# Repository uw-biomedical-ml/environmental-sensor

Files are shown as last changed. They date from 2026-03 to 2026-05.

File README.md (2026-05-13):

# Environmental Sensor: Hardware and Firmware

> **🚧 Work in Progress:** This repository is currently under active development. Files and documentation are being added incrementally.

This repository is home to the hardware designs, wiring instructions, and firmware source code for the environmental sensor project developed as part of the AI-READI initiative. 

## Publication & Project Context 

To support the AI-READI initiative's goal of making AI-ready data generation tools available to everyone, we are sharing the hardware designs, 3D enclosure (case) design files, and firmware mentioned in our upcoming paper. These resources are here for you to use, modify, and build upon. We invite you to download the code and design files and assemble your own sensor.

* 📄 **Paper:** *[Link to published paper will be added here]*
* 📊 **Supplement:** *[Link to supplementary materials will be added here]*

**Note on Scope:** This repository is strictly focused on the technical implementation of the sensor's physical build and microcontroller programming. For overarching project details, data analysis methodologies, and general information, please visit [aireadi.org](https://aireadi.org). We intentionally do not duplicate that information here. 

**No Research Approval Implied:** The AIREADI project was approved by an institutional review board to collect data from the homes of human participants. This approval, which is referenced in the [AIREADI Healthsheet](https://docs.aireadi.org/docs/3/dataset/healthsheet#collection-process), does not extend approval for any other entity to use this device in research with human participants without obtaining the permissions relevant to their proposed research.

## Repository Structure

### 1. `/firmware`
Contains the microcontroller code for the ESP32-S2.
* **`/sensor`:** The main program that initializes components, runs the primary data collection loop, and writes outputs to the SD card.
* **`/rtc`:** A standalone utility used strictly for setting the correct time on the precision RTC board.

### 2. `/hardware`
Contains the physical specifications, BOMs, and 3D files for the sensor build. *(The bill of materials files are available now; others will be uploaded soon).*
* **BOMs:** `BOM_electronics.md` (required electronics) and `BOM_assembly.md` (optional case hardware) list the necessary components.
* **`/wiring`:** Diagrams, schematics, and photos for connecting the electronics. *We highly recommend starting here to test your components before printing the case.*
* **`/enclosure`:** 3D printable files (STLs) for the 6-piece external case and internal PLA component trays, along with physical assembly notes.
* **`/board_models`:** 3D reference models (digital twins) of the electronic boards for those looking to design custom CAD enclosures.

## Getting Started Workflow

If you are building a sensor from scratch, we recommend the following sequence:

1. **Source Components:** Gather the required parts listed in `/hardware/BOM_electronics.md`.
2. **Wire and Test:** Follow the guides in `/hardware/wiring` to connect the electronics on your desk. 
3. **Flash Firmware:** Navigate to the `/firmware` directory to install the required libraries, set the RTC clock, and flash the main sensor code to verify the hardware is communicating properly.
4. **Assemble the Case:** Once the bare electronics are functioning, gather the hardware from `/hardware/BOM_assembly.md` and follow the instructions in `/hardware/enclosure` to print and assemble the physical unit.

---
*For general project information, please visit [aireadi.org](https://aireadi.org).*

## License and Citation

The hardware designs, firmware, and documentation in this repository are licensed under the [MIT License](LICENSE), with the following exceptions located in the `/hardware/board_models` directory:
* **`light.stl` and `metro.stl`:** Licensed under MIT License Copyright (c) 2016 Adafruit Industries.
* **`tft.stl`:** Licensed under Creative Commons Attribution-ShareAlike 3.0 Adafruit Industries.
* **`sen55.stl`:** This derivative STL part is included by permission from Sensirion Inc. Global Technical Support. Please see Sensirion's publicly available SEN55 STEP file for definitive information on the SEN55 component.

*(Please see the `README.md` or license files within the `/hardware/board_models` directory for the full text of these specific licenses).*

If you use these hardware designs, firmware, or documentation in your research, please cite our paper:

**🚧 Our paper is making its way through the publishing process...we will update this when we have final information.**

> **[Authors]. (2026). [Title of the AI-READI Environmental Sensor Paper]. [Journal/Conference Name]. [DOI/Link]**

**BibTeX:**
```bibtex
@article{aireadi_sensor_2026,
  title={Title of the AI-READI Environmental Sensor Paper},
  author={Lastname, Firstname and Lastname, Firstname},
  journal={Journal Name},
  year={2026},
  publisher={Publisher}
}

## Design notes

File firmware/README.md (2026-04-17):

# Firmware

This directory contains the microcontroller code for the environmental sensor. The firmware is divided into two separate sketches: a utility for configuring the Real-Time Clock (RTC) and the main sensor program.

## Directory Structure

### 1. RTC Adjustment Utility (`/rtc`)
The `rtc.ino` sketch is a standalone utility used strictly for programming the current date and time into the RTC board. 
* Please refer to the `README.md` located inside the `/rtc` folder for specific instructions on how to flash and set the clock before running the main sensor code.

### 2. Main Sensor Program (`/sensor`)
The `sensor.ino` sketch contains the primary operating logic for the device. 
* **Initialization:** Checks that all hardware components and sensors are present and responding.
* **Main Loop:** Queries the connected components at set intervals and writes the logged data to output files on the local SD card.

## Required Libraries

This project relies on several open-source libraries. You will need to install these via your Arduino Library Manager (or your preferred IDE) before compiling the sketches. No external libraries are bundled within this repository.

Search for and install the following libraries (we recommend installing any missing dependencies if the IDE prompts you to do so). The versions we report here were used with the hardware we selected; newer versions may also be acceptable.

* **RTClib** version 2.1.4 (by Adafruit) - *Required by both `rtc.ino` and `sensor.ino`*
* **Adafruit GFX Library** version 1.12.1
* **Adafruit ILI9341** version 1.6.2
* **Adafruit FT6206 Library** version 1.1.0
* **Adafruit AS7341** version 1.4.1
* **Adafruit TouchScreen** version 1.1.5
* **SdFat - Adafruit Fork** version 2.3.54 *(Note: Ensure you use the Adafruit fork of the SdFat library for compatibility)*
* **Sensirion I2C SEN5X** version 0.3.0

### related and/or dependent libraries
* **Adafruit BusIO** version 1.17.2
* **Wire** version 3.2.1
* **SPI** version 3.2.1
* **esptool.py** v4.8.1
* **Sensirion Core** version 0.7.1

## SD Card Preparation

Before running the main sensor firmware, we recommend preparing your SD card:
* For optimal compatibility and performance with the `SdFat` library, we highly recommend formatting your SD card to **ExFAT** (though it will generally work with standard FAT formats as well).
* Insert the card into your computer and use your operating system's default disk utility to format it.
* Once formatted, insert the SD card into the slot on your hardware before powering on the sensor. The `sensor.ino` script will automatically create the required log files on the card at startup.

## Setup and Flashing

1. Install the required libraries listed above.
2. First, open and flash `/rtc/rtc.ino` to set the correct time on the hardware. (See `/rtc/README.md` for details).
3. Once the RTC is set, open `/sensor/sensor.ino`, compile, and flash it to the microcontroller to begin normal data collection.

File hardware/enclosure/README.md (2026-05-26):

# Hardware / Enclosure
🚧 Work in Progress: This repository is currently under active development. Files and documentation are being added incrementally.

This directory contains the design files need to order parts for the sensor enclosure and component tray.

### 1. Component tray versions (*.stl)

* v1 - original design used by the research project
* v2 - next generation tray to resolve fragility of the SEN-55 guides

### 2. Acrylic enclosure (*.dxf)

All 6 *.dxf original files for the enclosure used by the research project.

* "front" -- refers to the side with the cutouts for power, most often in the back of the images we've provided
* "back" -- refers to the side dominate by horizontal vents and connection tabs along the full top edge, most often in the front of the images we've provided
* "sen55" -- the side with the design guide compliant openings for the SEN55 input and output ports
* "ani-sen55" -- the side opposite the SEN55
* "bot" -- the bottom
* "top" -- the top L-shaped panel with the cut-out for the touchscreen display
  
Caution: we may swap the front/back naming to align with drawings and photographs

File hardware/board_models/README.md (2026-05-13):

# Reference Board Models

> **🚧 Work in Progress:** This repository is currently under active development. Files and documentation are being added incrementally.

This directory contains 3D reference models (digital twins) of the physical electronic components used in the environmental sensor. 

**Note:** These files are provided strictly as dimensional references for use in CAD software to help you design custom enclosures or modify our existing case. They are *not* intended to be 3D printed.

## Reference STL Files

* **`metro.stl`:** Reference model for the main MCU board. 
* **`tft.stl`:** Reference model for the 2.8" TFT Touchscreen. 
* **`light.stl`:** Reference model for the AS7341 10-Channel Spectral Sensor.
* **`sen55.stl`:** Reference model (derivative) for the Sensirion SEN55 particle sensor. A STEP file can be found on the Sensirion website for the [SEN55]( https://sensirion.com/products/catalog/SEN55 ). Direct link: [SEN5x STEP file](https://sensirion.com/resource/cad/sen5x).

## Licensing Exceptions

While the majority of the hardware designs, firmware, and documentation in this repository are openly licensed under the MIT License, some of the 3D reference models in this directory are subject to different terms:

* **`light.stl` and `metro.stl`:** Licensed under MIT License Copyright (c) 2016 Adafruit Industries. Please see the `LICENSE-light-metro.txt` file in this directory for full terms.
* **`tft.stl`:** Licensed under Creative Commons Attribution-ShareAlike 3.0 Adafruit Industries. Please see the `LICENSE-tft.stl` file in this directory for full terms.
  
* * **`sen55.stl`:** This derivative STL part is included by permission from Sensirion Inc. Global Technical Support. Please see Sensirion's publicly available SEN55 STEP file for definitive information on the SEN55 component.

Please ensure you review the relevant license files if you plan to redistribute or modify these specific CAD models.

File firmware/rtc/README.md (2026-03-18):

# RTC Time Adjustment

This utility is used strictly to program the current date and time onto the Real-Time Clock (RTC) board. 

You only need to use this script when:
* The very first battery is placed into the slot on the RTC board.
* The battery has been removed and replaced.
* The time has drifted away from the current or target time.

## Equipment required
* A computer or laptop running the Arduino IDE. The instructions below were developed in IDE version 2.3.6 on macOS Version 15.5 (Sequoia). Install the IDE and load the required libraries (refer to the main [Firmware README](../README.md) for the complete list of dependencies).
* An MCU board (e.g. ESP32-S2) that will connect to the computer or laptop
* The real time clock RTC component to be programmed
* One 4-pin cable between the MCU and RTC
* One USB cable between the MCU and the computer / laptop

> **⚠️ WARNING for Existing Sensors:** Running this script will completely overwrite the firmware of the connected MCU. If you need to reset the RTC on an already-built sensor and want to preserve its existing firmware (e.g., to avoid breaking older library dependencies), **disconnect the RTC from the sensor's MCU** and use a separate, spare MCU to perform this programming.

> **💡 Tip for Batch Building:** If you are assembling multiple sensors and have spare hardware, it is highly convenient to reserve one MCU board exclusively for RTC programming. This avoids having to repeatedly flash the RTC adjustment script and then the main sensor firmware onto every individual sensor's ESP32.

## General instructions
* Connect the MCU board to the real time clock RTC component with the 4-pin cable
* Load the rtc.ino into the IDE
* Connect the MCU to the computer via USB-C and then select the MCU in the IDE
  * **Note:** The 12V power adapter is not required for this step; the USB-C connection provides sufficient power for programming the RTC.
* Compile and upload the *.ino file by pressing the arrow button at the top left of the IDE
* Manually open the Serial Monitor for messages and interactions by pressing the magnifying glass icon at the top right of the IDE

## Instructions for using the rtc.ino script
A few handy terms:

* compile_time: the time at which the *.ino script was compiled by the IDE
* laptop_time: the time showing on the computer doing the programming
* rtc_time: the time reported by the programmed RTC
* target_time: the target time for the RTC, e.g. local time, UTC time, or some other time

This version of the programming script will initially set the clock on the RTC to match the time at which the programming script was compiled (compile_time). The script will begin reporting the current RTC time (rtc_time) every 2 seconds in the output log of the Serial Monitor once it has been successfully programmed. In some cases, the rtc_time may differ from the laptop_time, the local time, or UTC time.

If the rtc_time is not sufficiently close to the target_time, then the dialog box of the Serial Monitor window can be used to send commands to the RTC to make adjustments by skipping forward or backward. Remember to press "Return" after entering the command. Any unknown commands entered will cause the list of available commands to be shown on screen.

### Available adjustment commands:

* f - adds  5 seconds to the rtc_time
* m - adds  1 minute  to the rtc_time
* n - adds 10 minutes to the rtc_time (i.e. a nap)
* h - adds  1 hour    to the rtc_time (60 minutes)
* b - subtracts 1 hour from the rtc_time (-60 minutes)

Date roll-overs (both forward and backward) are correctly handled by the rtc.adjust() function used in the script; only the time increment commands shown above are needed.

To set UTC time, an online site such as
* https://www.timeanddate.com/worldclock/timezone/utc

can be used as a reference while deciding on adjustments.

Once the rtc_time is sufficiently close to the target_time, the device can be powered off and disconnected from the MCU. Programming is complete.

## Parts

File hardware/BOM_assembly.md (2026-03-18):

# Assembly Bill of Materials

This list covers the mechanical hardware required to assemble the custom 3D-printed enclosure.

<table  align="left">
  <tr>
    <td valign="top"  align="left">
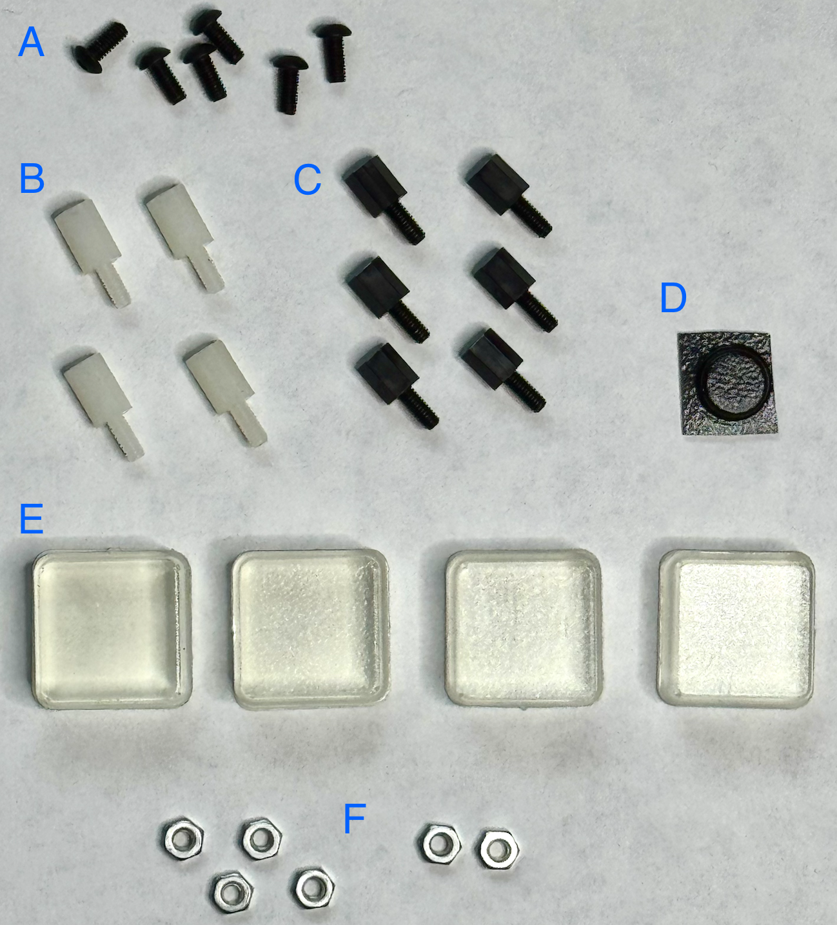
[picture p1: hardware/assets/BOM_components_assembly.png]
Assembly BOM Components
      
    </td>
    <td valign="top">
      <table>
        <tr><th align="center">Ref</th><th align="left">Description</th><th align="center">Qty</th></tr>
        <tr><td align="center"><b>A</b></td><td>M2.5 4mm screw</td><td align="center">6</td></tr>
        <tr><td align="center"><b>B</b></td><td>M2.5 8+6 standoff</td><td align="center">4</td></tr>
        <tr><td align="center"><b>C</b></td><td>M2.5 6+6 standoff</td><td align="center">6</td></tr>
        <tr><td align="center"><b>D</b></td><td>SEN55 top bumper</td><td align="center">1</td></tr>
        <tr><td align="center"><b>E</b></td><td>Standoff feet</td><td align="center">4</td></tr>
        <tr><td align="center"><b>F</b></td><td>M2.5 nuts</td><td align="center">6</td></tr>
      </table>
    </td>
  </tr>
</table>

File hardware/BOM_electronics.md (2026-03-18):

# Electronics Bill of Materials

| Component | Model / Description | Source / Link | Qty | Function & Notes |
| :--- | :--- | :--- | :---: | :--- |
| **MCU** | ESP32-S2 | [Adafruit 4775](https://www.adafruit.com/product/4775) | 1 | Main microcontroller processing sensor data. Contains the barrel jack power port. |
| **TFT Display** | 2.8" TFT Touch screen | [Adafruit 1947](https://www.adafruit.com/product/1947) | 1 | Minimal user interface (tap to wake display). Pairs directly with the MCU board. Contains the SD card slot.|
| **Particle Sensor** | Sensirion SEN55 | [Sensirion SEN55](https://sensirion.com/products/catalog/SEN55) | 1 | Measures particulate matter, VOCs, NOx, temperature and relative humidity. |
| **Spectral Sensor** | AS7341 10-Channel Light / Color Sensor | [Adafruit 4698](https://www.adafruit.com/product/4698) | 1 | Measures visible and near-infrared (NIR) light spectra. |
| **Adapter Board** | 3V to 5V level shifter for SEN55 | [Adafruit 5964](https://www.adafruit.com/product/5964) | 1 | Safely steps up logic voltage for the SEN55. |
| **Real Time Clock** | Precision RTC - Adafruit DS3231 | [Adafruit 3013](https://www.adafruit.com/product/3013) | 1 | Maintains system time (+/- 1 min/year, 2-5yr battery life). Reports internal temperature.|
| **Cable** | STEMMA QT / Qwiic JST SH 4-Pin - 50mm | [Adafruit 4399](https://www.adafruit.com/product/4399) | 3 | Connects I2C components. |
| **Cable** | 6-pin SEN55 cable | Custom (Similar: [Adafruit 5754](https://www.adafruit.com/product/5754)) | 1 | Connects SEN55 to the level shifter. |
| **Battery** | CR1220 | Local hardware/electronics store | 1 | Retains RTC time when unplugged. Without it, the clock resets on every startup. |
| **SD card** | Sandisk 32GB Micro SDHC Ultra Class 10 | Local electronics retailer | 1 | Stores output data files. (Recommend reformat to ExFAT before use.)|
| **Wall plug** | 12V barrel jack; center positive | Local electronics retailer | 1 | Power supply. Plugs into the barrel jack port on the MCU board. (A 6V adapter works, but 12V was used for all project data validation). |

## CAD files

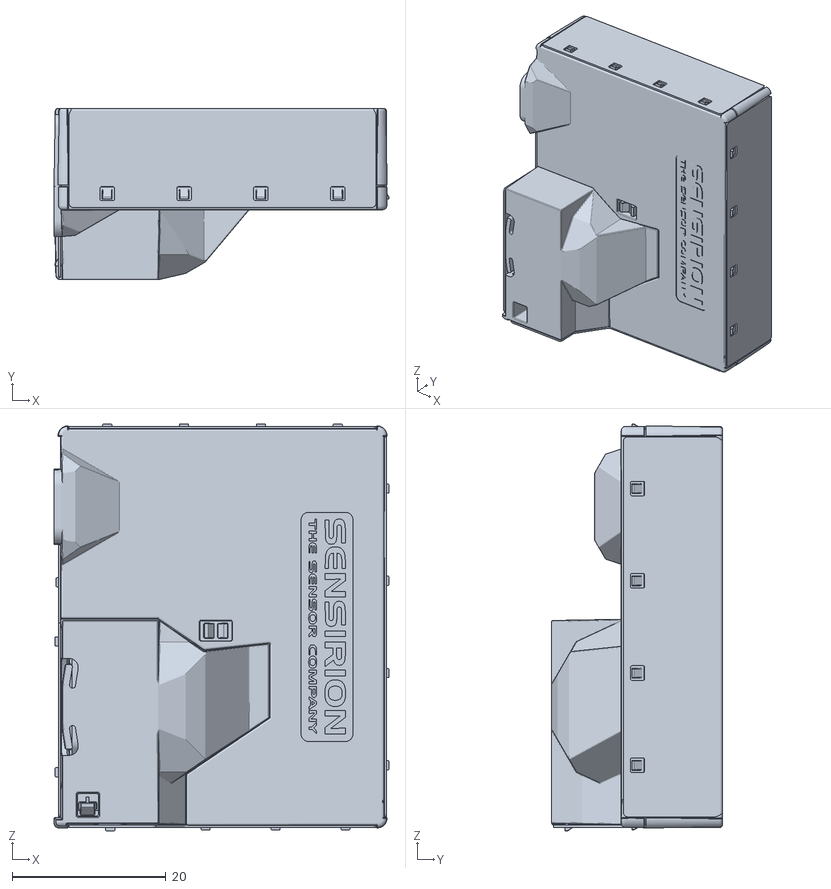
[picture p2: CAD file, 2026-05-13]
hardware/board_models/sen55.stl
43.6 x 22.3 x 52.9

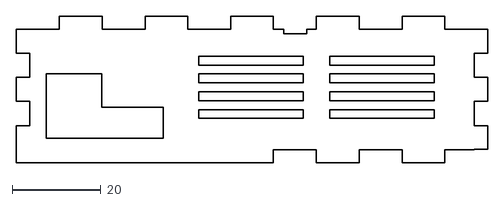
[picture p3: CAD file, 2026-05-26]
hardware/enclosure/front.dxf
106.0 x 33.0

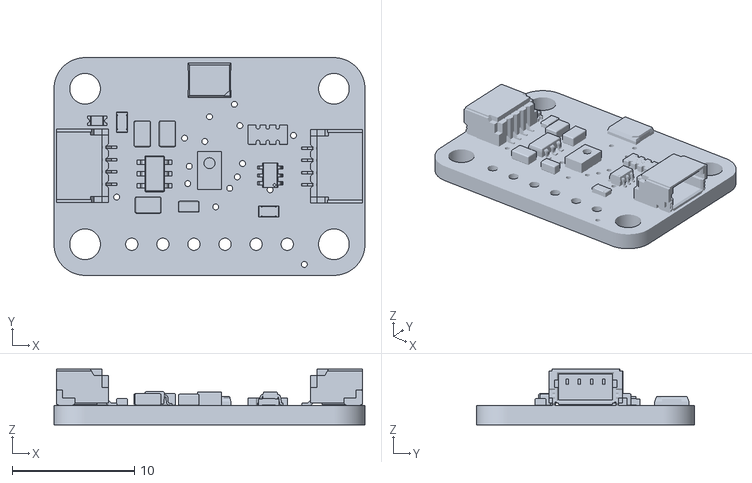
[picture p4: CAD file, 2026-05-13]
hardware/board_models/light.stl
25.4 x 17.8 x 4.55

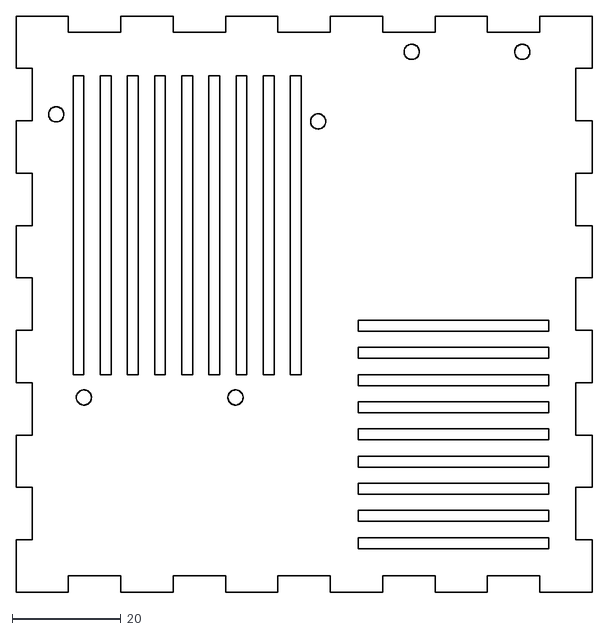
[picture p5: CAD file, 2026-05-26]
hardware/enclosure/bot.dxf
106.0 x 106.0

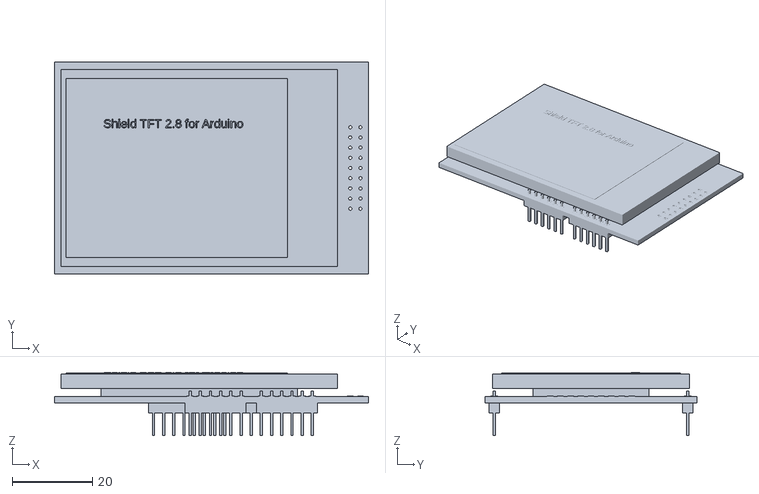
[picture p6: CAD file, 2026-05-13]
hardware/board_models/tft.stl
78.3 x 52.8 x 15.8

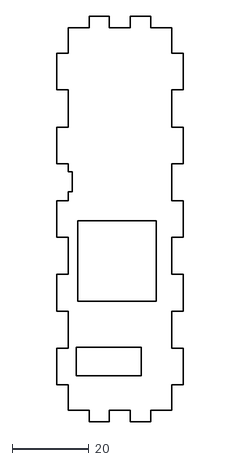
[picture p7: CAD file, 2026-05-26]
hardware/enclosure/sen.dxf
33.0 x 106.0

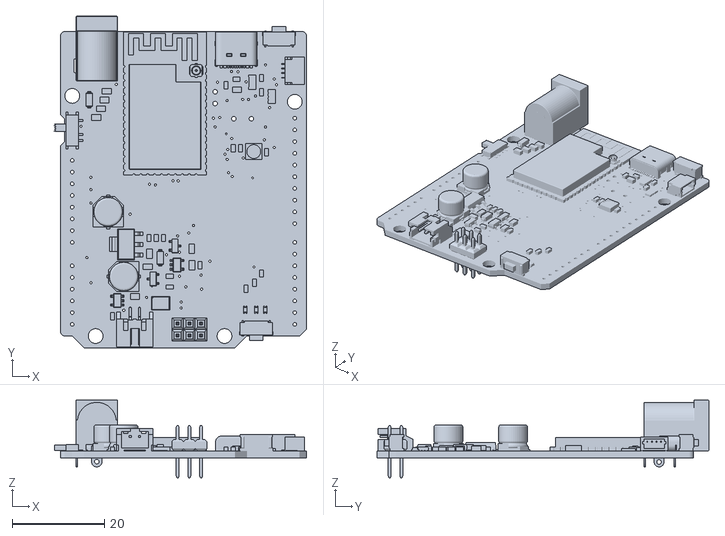
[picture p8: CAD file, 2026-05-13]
hardware/board_models/metro.stl
54.6 x 71.9 x 16.9

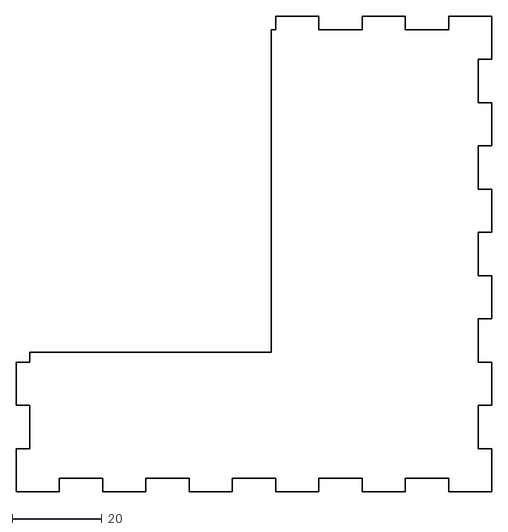
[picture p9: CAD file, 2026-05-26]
hardware/enclosure/top.dxf
106.0 x 106.0

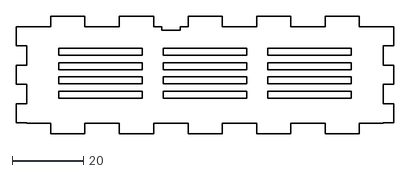
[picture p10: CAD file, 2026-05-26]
hardware/enclosure/back.dxf
106.0 x 33.0

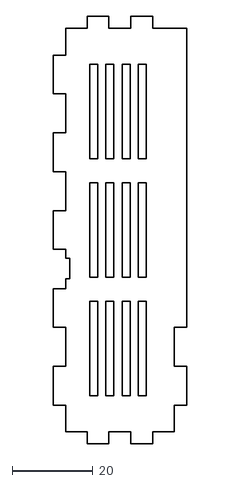
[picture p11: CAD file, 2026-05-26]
hardware/enclosure/anti-sen55.dxf
33.0 x 106.0

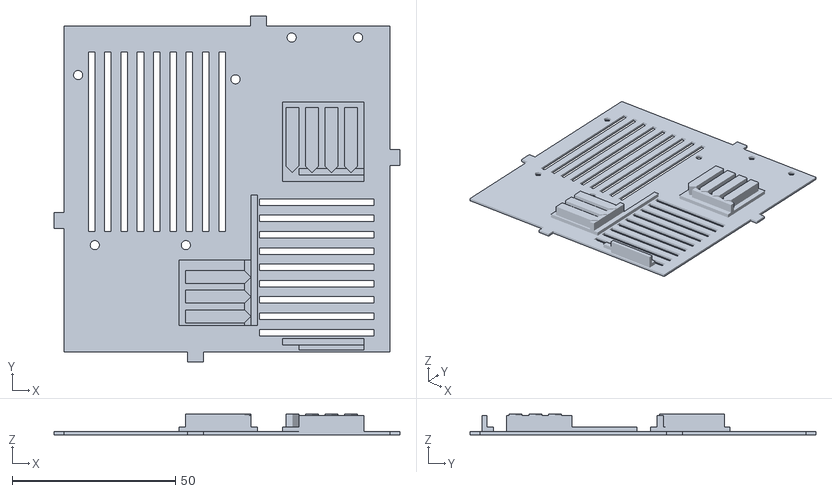
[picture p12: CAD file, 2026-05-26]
hardware/enclosure/tray_v2.stl
106.0 x 106.0 x 6.40

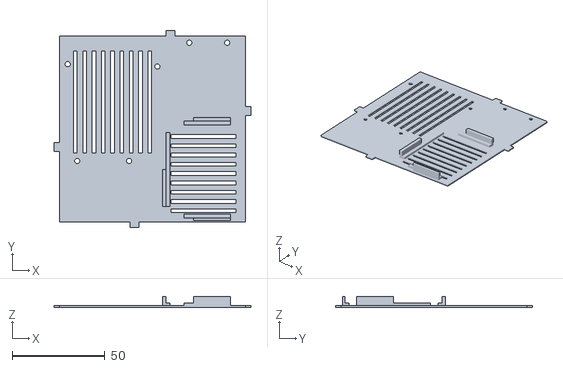
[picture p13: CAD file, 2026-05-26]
hardware/enclosure/tray_v1.stl
106.0 x 106.0 x 6.00

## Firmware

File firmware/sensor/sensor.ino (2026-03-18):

#include "SPI.h"
#include <Adafruit_GFX.h>         // Core graphics library
#include <Adafruit_ILI9341.h>     // Hardware-specific library
#include <SdFat.h>                // SD card & FAT filesystem library (Adafruit's version)
#include <Adafruit_FT6206.h>

#include <SensirionI2CSen5x.h>
#include <Arduino.h>
#include <Wire.h>
#include <Adafruit_AS7341.h>

#include "TouchScreen.h"
#include "wiring_private.h"
#include "RTClib.h"
#include "sdios.h"

#define RTC_TYPE 1 // 0 = Old, 1= New high precision


ArduinoOutStream cout(Serial);

void cardOrSpeed() {
  cout << F("Try another SD card or reduce the SPI bus speed.\n");
  cout << F("Edit SPI_SPEED in this program to change it.\n");
}

// END TESTING

#define   VERSION   "1.2.4"

Adafruit_FT6206 ctp = Adafruit_FT6206();

SensirionI2CSen5x sen5x;
Adafruit_AS7341 as7341;

#if RTC_TYPE == 0
RTC_PCF8523 myRTC;
#elif RTC_TYPE == 1
RTC_DS3231 myRTC;
#endif

#define TFT_DC   14
#define TFT_CS   15
#define TFT_BACKLIGHT 10

Adafruit_ILI9341 tft = Adafruit_ILI9341(TFT_CS, TFT_DC); //, TFT_MOSI, TFT_CLK, TFT_RST, TFT_MISO);
#define SD_CS 9
unsigned char sen_product[48];
unsigned char sen_sn[48];
SdFs sd;
FsFile file;

char filename[20];
unsigned long screenTime = 0;
int screenStatus = 1; // 1 means on, 0 means off
unsigned long lastTime = 0;
unsigned long file_lines = 0;

void(* resetFunc) (void) = 0; 

void newLogFile() {

  DateTime now = myRTC.now();
  char buf2[] = "YYYYMMDDhhmmss";
  String temp = (String) now.toString(buf2) + ".csv";
  temp.toCharArray(filename, 20);
  file.open(filename,  O_RDWR | O_CREAT | O_AT_END);
  if (file) {
      Serial.println("; " + String((char *) sen_product) + " " + String((char *) sen_sn));
      file.println("; Version: " + String( VERSION ));
      file.println("; " + String((char *) sen_product) + " " + String((char *) sen_sn));
      if (RTC_TYPE == 0) {
        file.println("ts,lch0,lch1,lch2,lch3,lch6,lch7,lch8,lch9,lch10,lch11,pm1,pm2.5,pm4,pm10,hum,temp,voc,nox,screen,ff");
      } else if (RTC_TYPE == 1) {
        file.println("ts,lch0,lch1,lch2,lch3,lch6,lch7,lch8,lch9,lch10,lch11,pm1,pm2.5,pm4,pm10,hum,temp,voc,nox,screen,ff,inttemp");
      }
      
      file.close();
  } else {
      Serial.println("Could not write to file!");
      tft.println(sd.card()->errorCode());
      tft.println(sd.card()->errorData());
      while (1) { delay(100); }
  }
}

void setup(void) {
  Serial.begin(9600);
  
  //Wire.begin(0x08);
  // Turn on backlight (required on PyPortal)
  pinMode(TFT_BACKLIGHT, OUTPUT);
  digitalWrite(TFT_BACKLIGHT, HIGH);
  pinMode(TFT_CS, OUTPUT);
  pinMode(SD_CS, OUTPUT);
  digitalWrite(TFT_CS, LOW);
  digitalWrite(SD_CS, HIGH);
  delay(200);

  
  tft.begin();          // Initialize screen
  
  tft.fillScreen(ILI9341_BLACK);
  tft.setTextColor(ILI9341_WHITE);
  tft.setTextSize(2);
  tft.setTextWrap(true);
  tft.setCursor(0, 0);
  tft.println("Starting setup");

  /*************** Touchscreen ***************/
  Serial.print("Touchscreen...");
  tft.print("Touchscreen... ");
  
  if (! ctp.begin(40)) {  // pass in 'sensitivity' coefficient
      tft.setTextColor(ILI9341_RED);
      tft.println("failed!");
      Serial.println("Card init. failed!");
      Serial.flush();
      while (1) { delay(100); }
  } else {
      tft.setTextColor(ILI9341_GREEN);
      tft.println("OK");
      delay(500);
      Serial.println("OK!");
  }
  tft.setTextColor(ILI9341_WHITE);

  /*************** RTC ***************/
  Serial.println("RTC... ");
  tft.print("RTC... ");
  if (! myRTC.begin()) {
      tft.setTextColor(ILI9341_RED);
      tft.print("failed\n");
      delay(500);;
      Serial.println("Couldn't find RTC");
      Serial.flush();
      while (1) { delay(100); }
  } else {
      tft.setTextColor(ILI9341_GREEN);
      tft.println("OK");
      delay(500);
      Serial.println("OK!");
  }
  tft.setTextColor(ILI9341_WHITE);  
  Serial.println("RTC started...");

  /*************** SD CARD ***************/
  
  Serial.print("SD Card...");
  tft.print("SD card... ");

  digitalWrite(TFT_CS, HIGH);
  delay(200);
  if (!sd.begin(SD_CS, SD_SCK_MHZ(10))) { // v1.2.4 new fix from 25 to 10
      tft.setTextColor(ILI9341_RED);
      tft.println("failed!");
      tft.println(int(sd.sdErrorCode()));
      tft.println(int(sd.sdErrorData()));
      Serial.println("Card init. failed!");
      Serial.flush();
      while (1) { delay(100); }
  } else {
      // TESTING

  uint32_t size = sd.card()->sectorCount();
  if (size == 0) {
    cout << F("Can't determine the card size.\n");
    cardOrSpeed();
    return;
  }
  uint32_t sizeMB = 0.000512 * size + 0.5;

  
  cout << F("Card size: ") << sizeMB;
  cout << F(" MB (MB = 1,000,000 bytes)\n");
  cout << endl;
  cout << F("Volume is FAT") << int(sd.vol()->fatType());
  cout << F(", Cluster size (bytes): ") << sd.vol()->bytesPerCluster();
  cout << endl << endl;
  cout << F("Files found (date time size name):\n");
  sd.ls(LS_R | LS_DATE | LS_SIZE);
      // END TESTING
      
            
      tft.setTextColor(ILI9341_GREEN);
      tft.println("OK");
      delay(500);
      Serial.println("OK!");
  }
  tft.setTextColor(ILI9341_WHITE);

  

  /*************** SEN 5X ***************/
  Serial.println("SEN 5x... ");
  tft.print("SEN 5x... ");
  sen5x.begin(Wire);
  uint16_t error;
  char errorMessage[256];
  error = sen5x.deviceReset();
  if (error) {
        Serial.print("Error trying to execute deviceReset(): ");
        errorToString(error, errorMessage, 256);
        Serial.println(errorMessage);
        tft.setTextColor(ILI9341_RED);
        tft.print("failed\n");
        Serial.flush();
        while (1) { delay(100); }
  } else {
      tft.setTextColor(ILI9341_GREEN);
      tft.println("OK");
      delay(500);
      Serial.println("OK!");
  }
  tft.setTextColor(ILI9341_WHITE);


  Serial.println("Setting / cleaning SEN 5x... ");
  tft.print("Setting / cleaning SEN 5x... ");

  sen5x.startFanCleaning();

  float tempOffset = 0.0;
    error = sen5x.setTemperatureOffsetSimple(tempOffset);
    if (error) {
        Serial.print("Error trying to execute setTemperatureOffsetSimple(): ");
        errorToString(error, errorMessage, 256);
        Serial.println(errorMessage);
        tft.setTextColor(ILI9341_RED);
        tft.print("failed\n");
        Serial.flush();
        while (1) { delay(100); }
    } else {
        Serial.print("Temperature Offset set to ");
        Serial.print(tempOffset);
        Serial.println(" deg. Celsius");

        tft.setTextColor(ILI9341_GREEN);
        tft.println("OK");
        delay(500);
        Serial.println("OK!");
    }
    tft.setTextColor(ILI9341_WHITE);

  Serial.println("Testing SEN 5x... ");
  tft.print("Testing SEN 5x... ");

  sen5x.getProductName(sen_product, 48);
  sen5x.getSerialNumber(sen_sn, 48);

  error = sen5x.startMeasurement();
    if (error) {
        Serial.print("Error trying to execute startMeasurement(): ");
        errorToString(error, errorMessage, 256);
        Serial.println(errorMessage);

        
        tft.setTextColor(ILI9341_RED);
        tft.print("failed\n");
        Serial.flush();
        while (1) { delay(100); }
    } else {
        tft.setTextColor(ILI9341_GREEN);
        tft.println("OK");
        delay(500);
        Serial.println("OK!");
    }
    tft.setTextColor(ILI9341_WHITE);


  /*************** SPECTRUM ***************/   
  Serial.println("Spectral sensor... ");
  tft.print("Spectral sensor... "); 
    if (!as7341.begin()){
      Serial.println("Could not find AS7341");

        tft.setTextColor(ILI9341_RED);
        tft.print("failed\n");
        Serial.flush();
        while (1) { delay(100); }
    } else {
        
        tft.setTextColor(ILI9341_GREEN);
        tft.println("OK");
        delay(500);
        Serial.println("OK!");
    }
    tft.setTextColor(ILI9341_WHITE);    
    as7341.enableLED(false);
    as7341.setATIME(100);
    as7341.setASTEP(999);
    as7341.setGain(AS7341_GAIN_256X);


  newLogFile();
    
  tft.println("\nAll finished!");
  delay(1000); // Pause 2 seconds before moving on to loop()
  tft.fillScreen(ILI9341_BLACK);
  tft.setTextColor(ILI9341_WHITE, ILI9341_BLACK);

  screenTime = micros();
  lastTime = 0;
  file_lines = 0;
  screenStatus = 1;
}
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

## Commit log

2026-03-18 add: sensor.ino
2026-05-13 add: hardware/board_models with stl for visualization
    [light.stl, metro.stl, sen55.stl, tft.stl]
2026-05-26 init: tray versions confirmed by 2026.05 fab & build
    [tray_v1.stl, tray_v2.stl]
2026-05-26 init: 6 acrylic w/ orig names confirmed by 2026.05 fab & build
    [anti-sen55.dxf, back.dxf, bot.dxf, front.dxf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]
